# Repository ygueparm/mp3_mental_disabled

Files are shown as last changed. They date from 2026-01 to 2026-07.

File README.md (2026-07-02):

# mp3 player for mental disabled
mp3_mental_disabled is a simplified MP3 speaker designed for people with intellectual disabilities. It focuses on ease of use, minimal controls, and clear audio playback. The project aims to provide an accessible, reliable, and stress-free music experience using simple hardware and software.

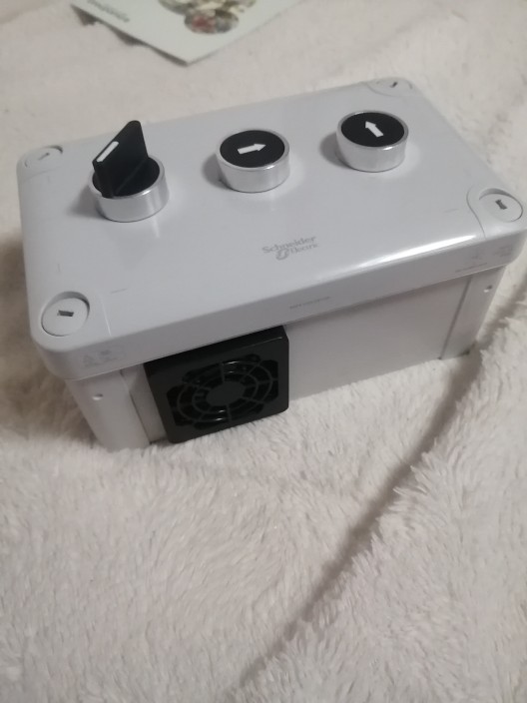
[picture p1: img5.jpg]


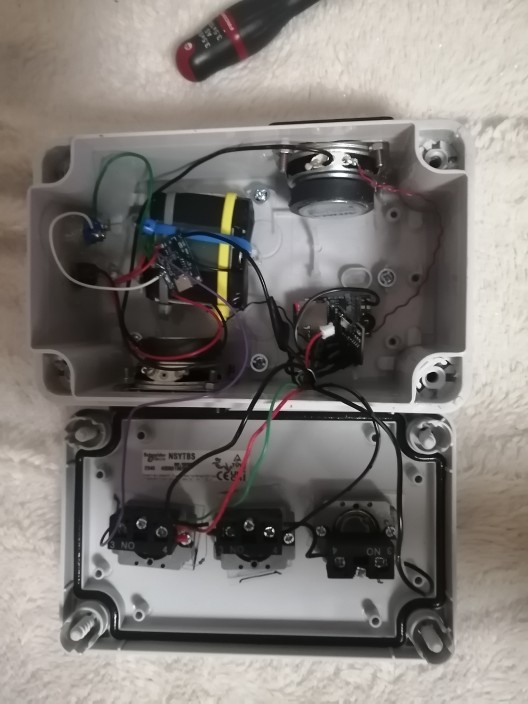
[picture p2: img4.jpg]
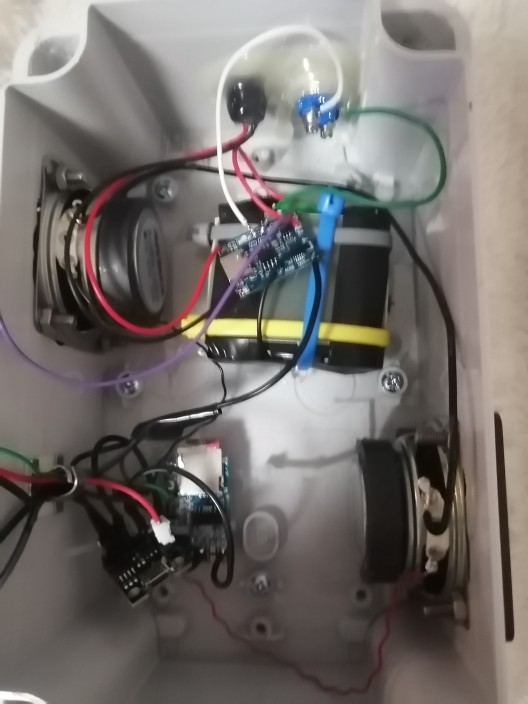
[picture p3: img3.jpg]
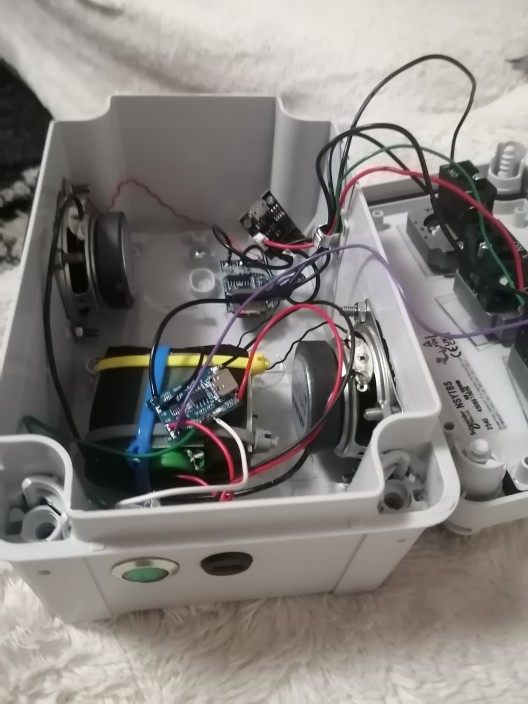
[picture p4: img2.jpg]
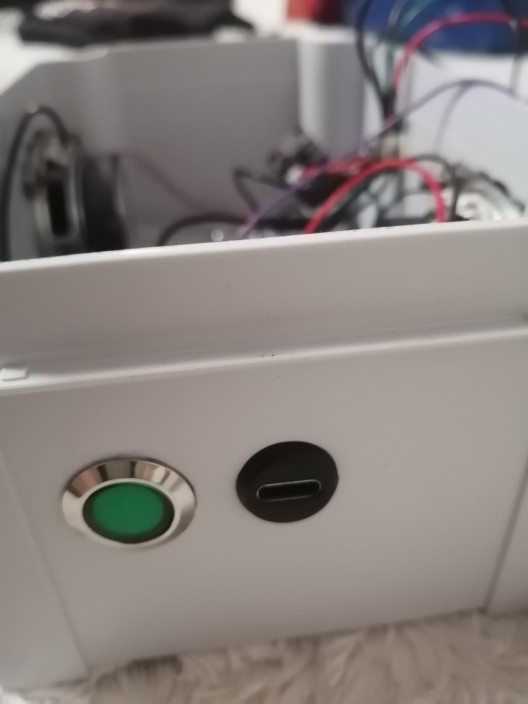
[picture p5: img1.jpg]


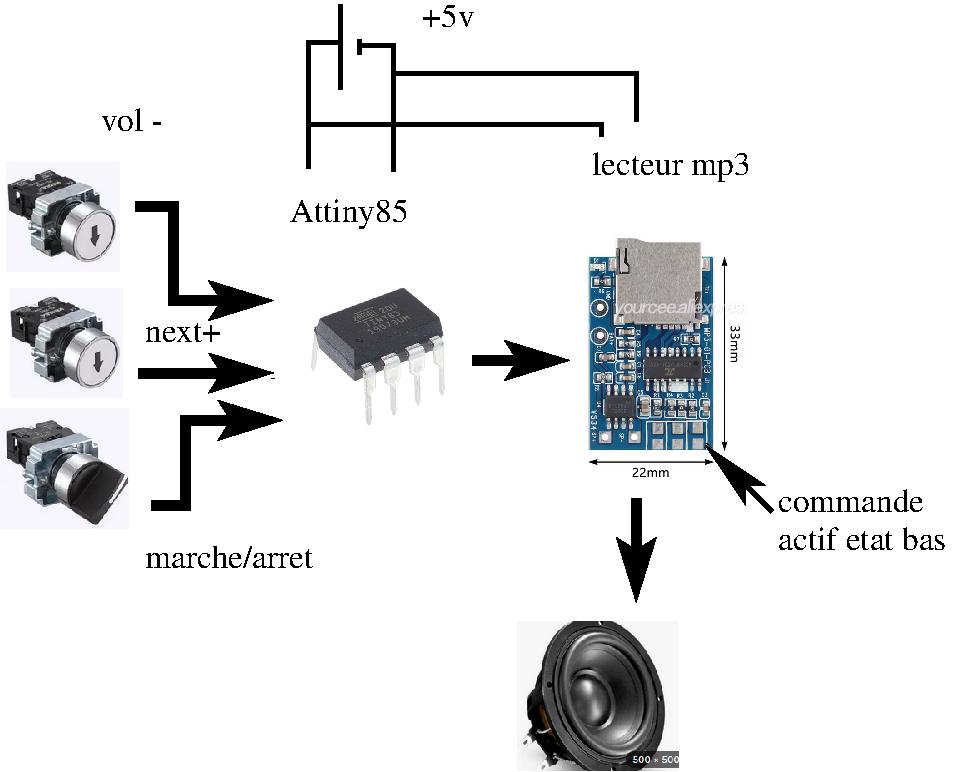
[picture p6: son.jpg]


##  MP3 Player for People with Mental Disabilities

One of my daughters is 80% mentally disabled. To give you an idea, at 20 years old she has the IQ of a 3-4 year old child.

She can learn certain things, but it takes quite a bit of time. We leave her an MP3 speaker because she loves listening to music.

The problem: These speakers have 3 buttons, and depending on how long you press them, the function changes. When she wants to change the song, she presses pretty much everything and switches the speaker to radio or Bluetooth mode, and I have to put it back in the right mode quite regularly. I don't have time for just that!

I'm using an Attiny85 as an interface between the MP3 PCB and the human to simulate the correct button presses and limit them to next+ and volume down.

I was inspired by jbd's journal at https://linuxfr.org/users/jbd/journaux/hacking-d-une-machine-a-pain
The point that was giving me trouble was using optocouplers. I found something better! No optocouplers needed!

Since the inputs are active low, I use the Tiny's LOW output, and for "no press" I set the pin as an input (so in high impedance state).

To pull to ground:
```
cpp

void setPinLow(uint8_t pin) {
  digitalWrite(pin, LOW);
  pinMode(pin, OUTPUT);
}

**Important:** set to LOW BEFORE switching to output mode

And to float (high impedance):
cpp

void setPinHighZ(uint8_t pin) {
  pinMode(pin, INPUT);
  digitalWrite(pin, LOW); // (just in case)
}
```

So no optocoupler and I'm using 4 pins out of 6 on the Tiny. At startup, I increase the volume, then I limit button presses.
The next track can only be selected after 5 seconds, so she actually listens a bit before changing :)

It's possible to completely mute the sound, but a simple power cycle restores the volume level.
To increase the volume more and more, just do several power cycles in a row.

In short: simple, effective, and it gives the person autonomy. If I tell her to stop the music, she can do it, change tracks, lower the volume too.

And she can stop it herself to go to sleep. IN SHORT: it's brilliant!

## list of equipment

### I particularly recommend the French manufacturer of polycarbonate boxes, which are resistant and unbreakable schneider electrique :
The cover is closed with four captive flat screws located outside the sealed area of the enclosure to maintain the IP rating. It is TÜV and UL certified and is fire resistant up to 960°C in accordance with IEC 62208. It offers high protection against dust and water with an IP66 rating (NEMA 4.4X). It is impact resistant (IK08 rating, IEC 62262). It also has Class II electrical insulation, which prevents electric shocks and offers fully insulated solutions. It can be stored at temperatures between -15 and 60°C and used between -25 and 80°C without affecting its performance. you can use it even in siberia ! :)

 *  https://www.se.com/fr/fr/product/NSYTBP16128/panelset-bo%C3%AEte-industrielle-164x121x87mm-pc/
 *  PanelSeT - boîte industrielle - 164x121x87mm - PCNSYTBP16128

 *  1Pcs Metal Round Socket Module
 *  https://fr.aliexpress.com/item/1005005363341111.html

 *  AIYIMA 2 pièces 2 "pouces 4 Ohm 3W gamme
 *  https://fr.aliexpress.com/item/32593991938.html

 *  https://fr.aliexpress.com/item/1005007445592831.html
 * 
 *  Ttiny85 Digispark Kickstarter Micro USB
 *  https://fr.aliexpress.com/item/1005009004637470.html

 *  Audio MP3 TF 2W 5V
 *  https://fr.aliexpress.com/item/1005009187267335.html

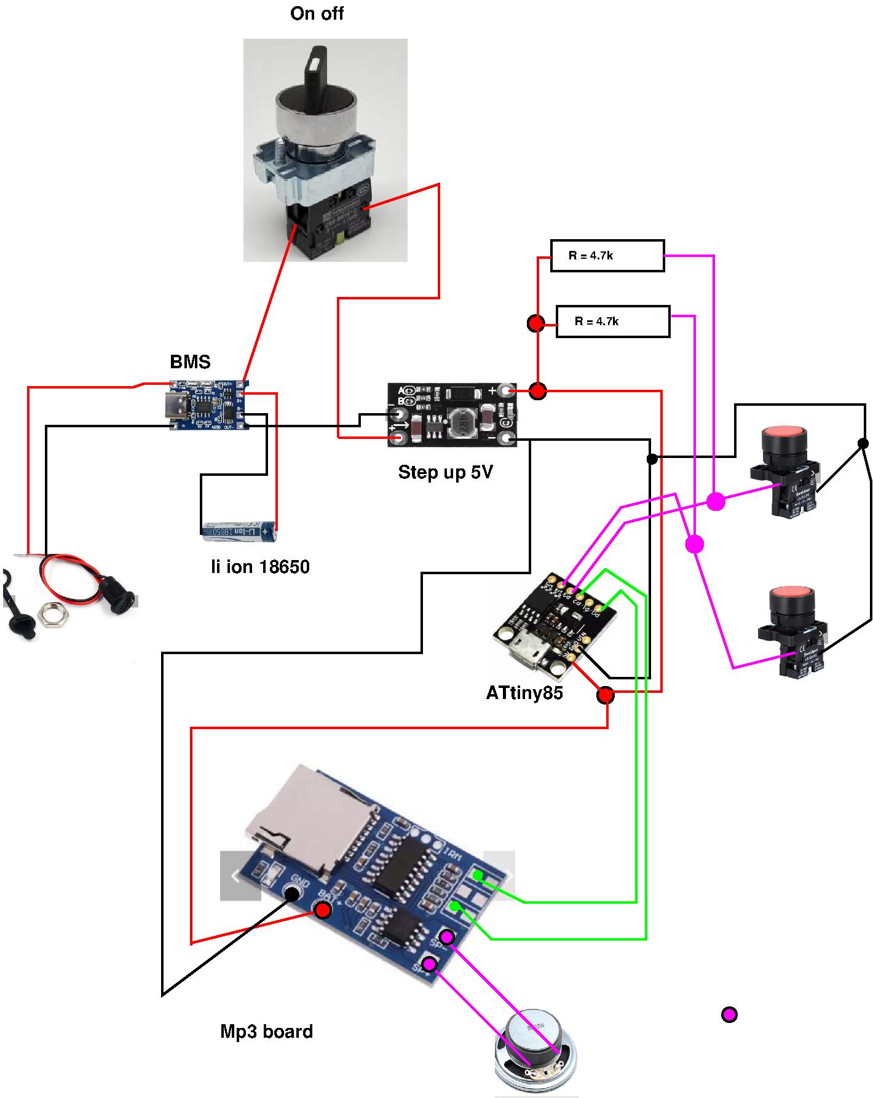
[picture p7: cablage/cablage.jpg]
blue print


Why choose the Tiny85? I always feel a bit bad using only 4 pins out of 40 on a microcontroller. Low power consumption, 1MHz speed, variable supply voltage. Very flexible to use and very cheap. A bit difficult to program because you need an Arduino in ISP mode as an interface between the Tiny and Arduino IDE.

# Small production
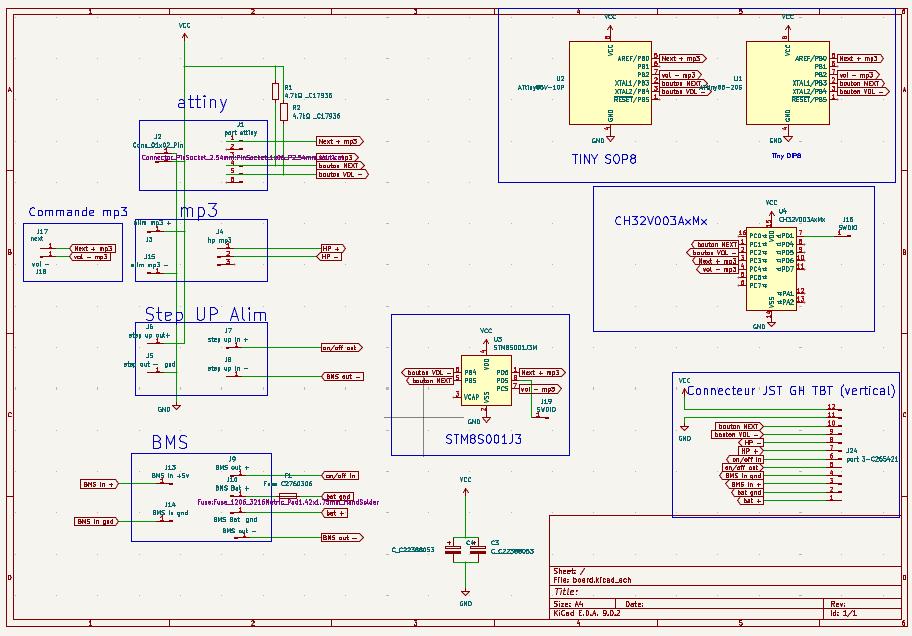
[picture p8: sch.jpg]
sch

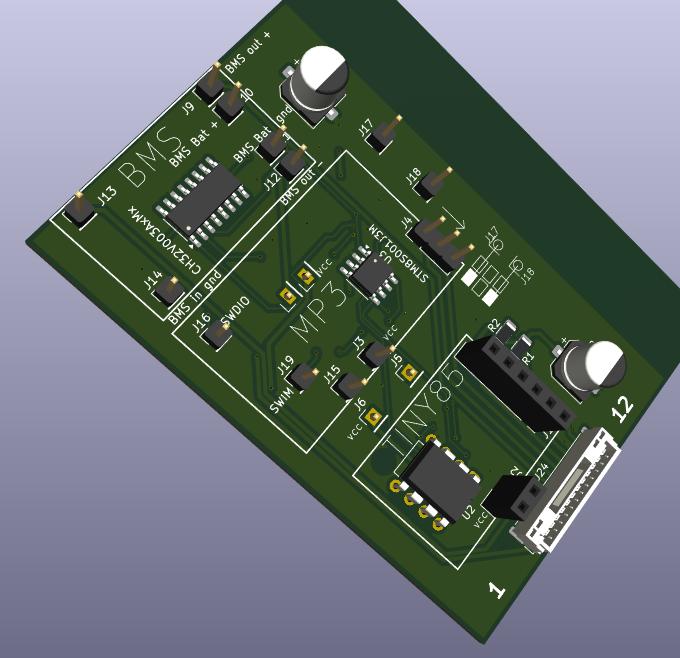
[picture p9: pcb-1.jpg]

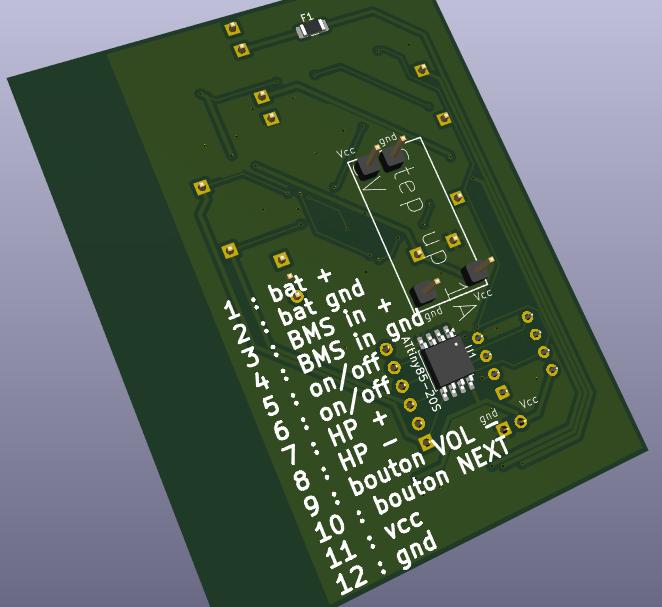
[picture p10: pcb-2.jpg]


Now the project is very well and my daughter is very happy but it take 2 to 3 hours to make one, for small production i made a mother board
for reduce the time for it. time to time and buold one for this friends, and some young children like it very much (2 to 5 years old) !

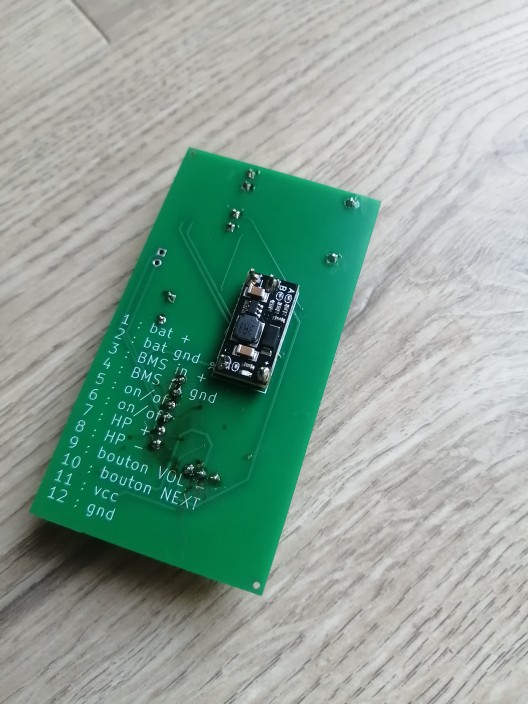
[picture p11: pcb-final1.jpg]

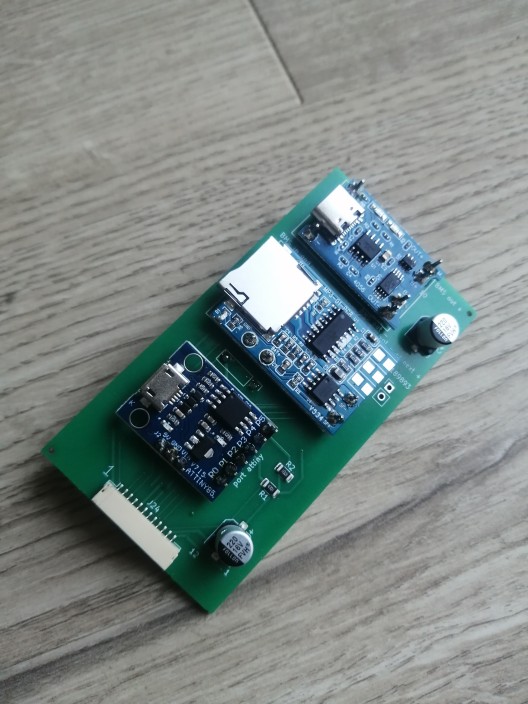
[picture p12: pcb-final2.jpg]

 
 this pcb can spped up your box, only 10 to 15 min to finish one instead 2 a 3h, this pcb let you choose wich chip you prefer, small board with Attiny85, chip attiny85, STM8, CH32V003A4M6, the last one cost only 0.20€ and you can use arduino-ide for programming it
 
 YOU NEED ONLY ONE OF THIS CHIP AT ONCE : attiny85, STM8, CH32V003A4M6 simply choose wich you prefer

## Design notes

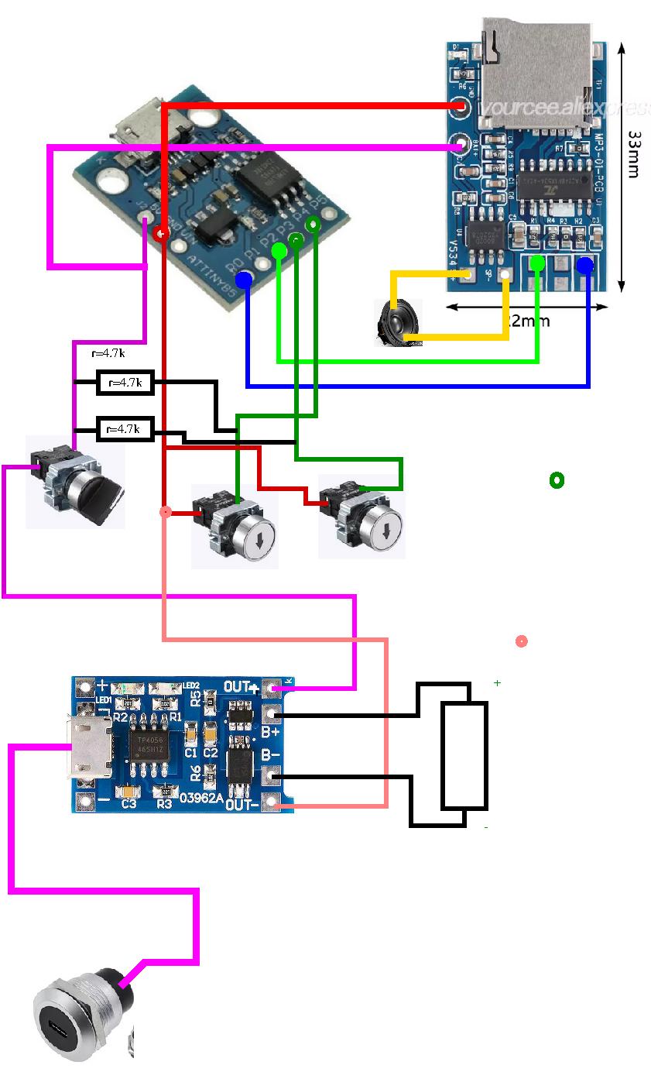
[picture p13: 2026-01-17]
plan.jpg

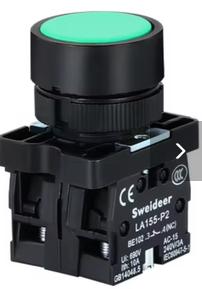
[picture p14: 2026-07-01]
cablage/bouton.jpg

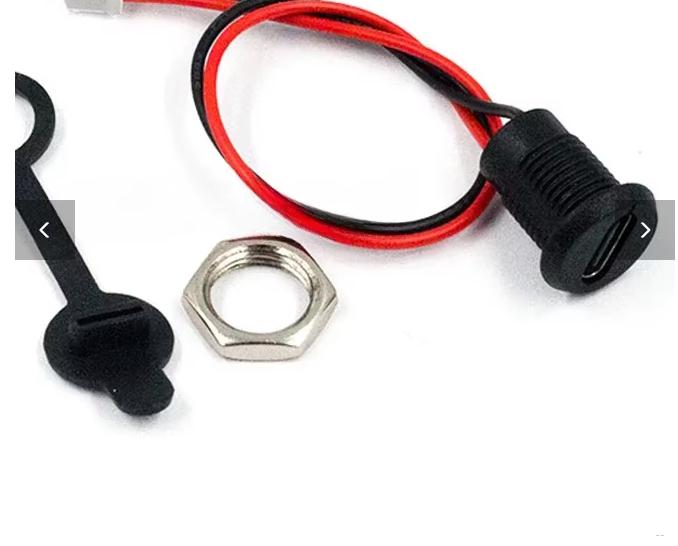
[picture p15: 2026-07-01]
cablage/usbc-prise.jpg

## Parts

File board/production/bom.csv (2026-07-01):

Designator | Footprint | Quantity | Value | LCSC Part #
C3, C4 | CP_Elec_6.3x7.7 | 2 | C_C22388053
F1 | 1206 | 1 | Fuse C2760306
J1 | PinSocket_1x06_P2.54mm_Vertical | 1 | port attiny
J10 | PinHeader_1x01_P2.54mm_Vertical | 1 | BMS Bat +
J11 | PinHeader_1x01_P2.54mm_Vertical | 1 | BMS Bat gnd
J12 | PinHeader_1x01_P2.54mm_Vertical | 1 | BMS out -
J13 | PinHeader_1x01_P2.54mm_Vertical | 1 | BMS in +5v
J14 | PinHeader_1x01_P2.54mm_Vertical | 1 | BMS in gnd
J15 | PinHeader_1x01_P2.54mm_Vertical | 1 | alim mp3 -
J16 | PinHeader_1x01_P2.54mm_Vertical | 1 | SWDIO
J17 | PinHeader_1x01_P2.54mm_Vertical | 1 | next
J18 | PinHeader_1x01_P2.54mm_Vertical | 1 | vol -
J19 | PinHeader_1x01_P2.54mm_Vertical | 1 | SWIM
J2 | PinSocket_1x02_P2.54mm_Vertical | 1 | Conn_01x02_Pin
J24 | JST_GH_BM12B-GHS-TBT_1x12-1MP_P1.25mm_Vertical | 1 | port 3-C265421
J3 | PinHeader_1x01_P2.54mm_Vertical | 1 | alim mp3 +
J4 | PinHeader_1x03_P2.54mm_Vertical-mp3 | 1 | hp mp3
J5 | PinHeader_1x01_P2.54mm_Vertical | 1 | step out - gnd
J6 | PinHeader_1x01_P2.54mm_Vertical | 1 | step up out+
J7 | PinHeader_1x01_P2.54mm_Vertical | 1 | step up in +
J8 | PinHeader_1x01_P2.54mm_Vertical | 1 | step up in -
J9 | PinHeader_1x01_P2.54mm_Vertical | 1 | BMS out +
R1, R2 | 1206 | 2 | 4.7kΩ _C17936
U1 | SOIC-8_5.3x5.3mm_P1.27mm | 1 | ATtiny85-20S
U2 | DIP-8_W7.62mm | 1 | ATtiny85V-10P
U3 | SO-8_3.9x4.9mm_P1.27mm | 1 | STM8S001J3M
U4 | SOP-16_3.9x9.9mm_P1.27mm | 1 | CH32V003AxMx

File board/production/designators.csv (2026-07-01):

C3:1
C4:1
F1:1
J1:1
J10:1
J11:1
J12:1
J13:1
J14:1
J15:1
J16:1
J17:1
J18:1
J19:1
J2:1
J24:1
J3:1
J4:1
J5:1
J6:1
J7:1
J8:1
J9:1
R1:1
R2:1
U1:1
U2:1
U3:1
U4:1

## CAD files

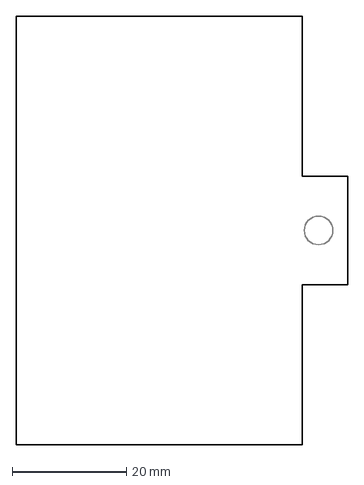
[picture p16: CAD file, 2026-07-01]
board/pcb.dxf
58.0 x 75.0 mm

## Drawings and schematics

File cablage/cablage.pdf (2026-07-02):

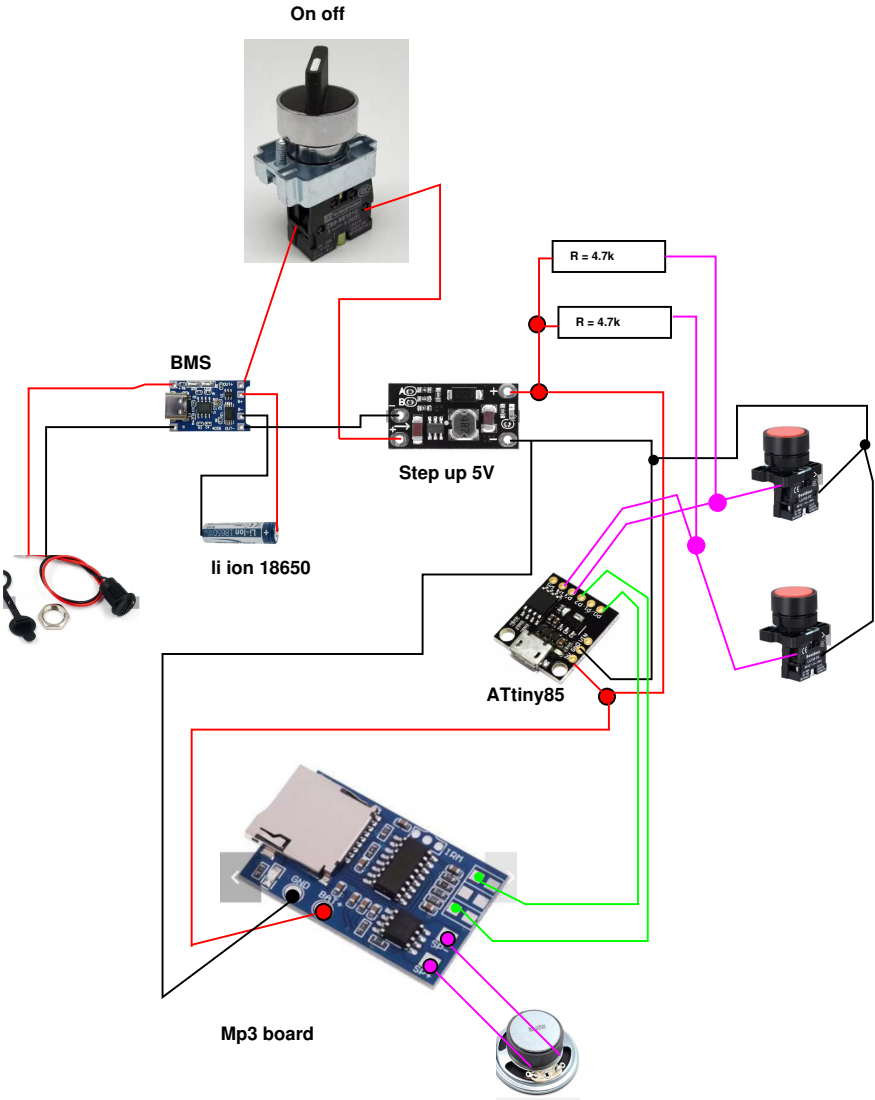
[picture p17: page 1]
Step up 5V; li ion 18650; Mp3 board; ATtiny85; BMS; On off

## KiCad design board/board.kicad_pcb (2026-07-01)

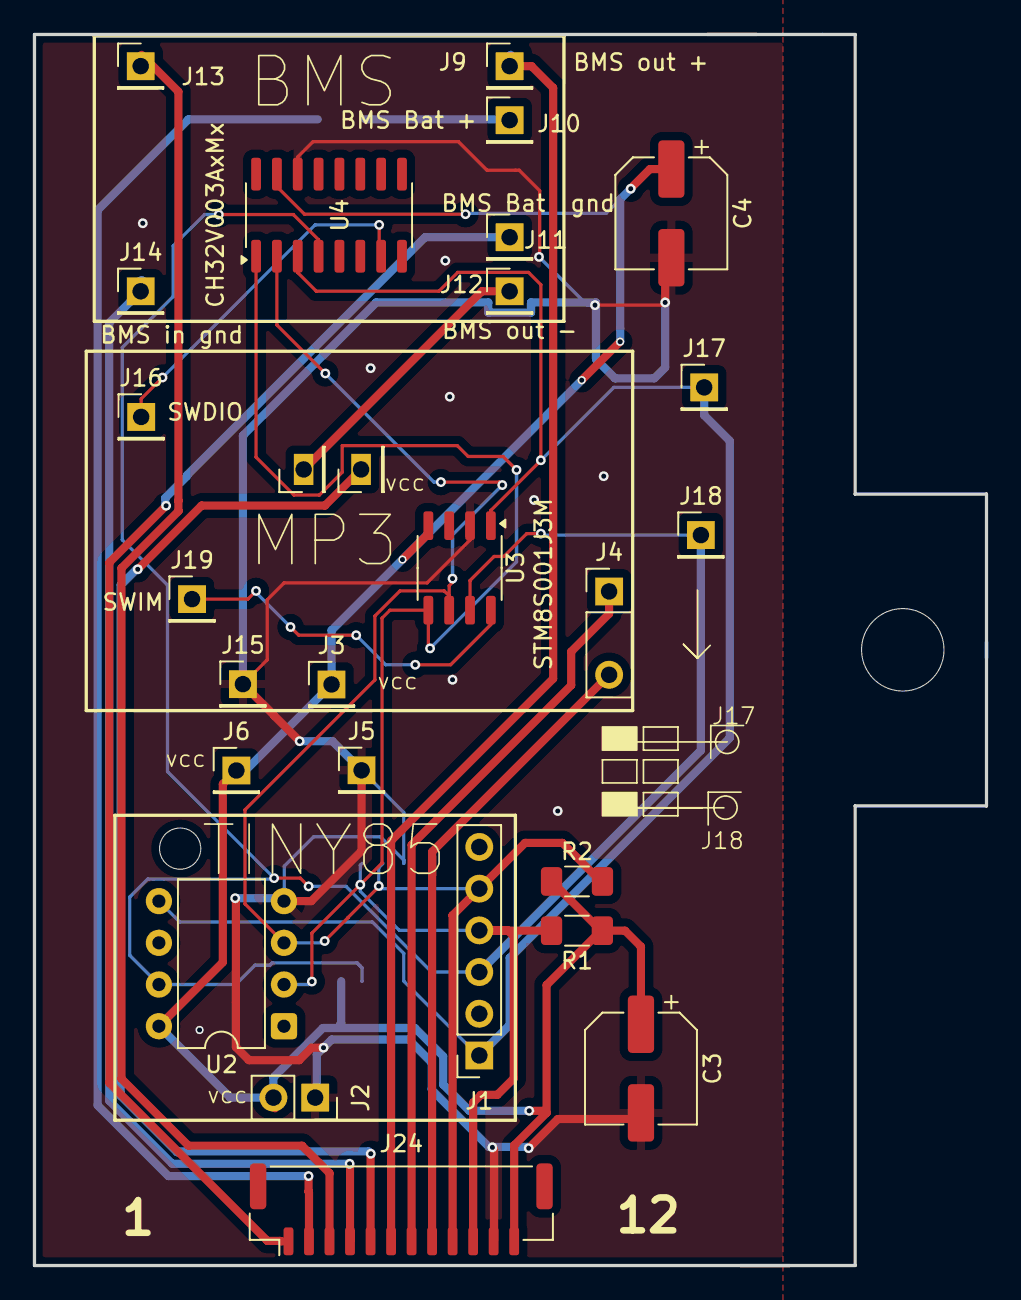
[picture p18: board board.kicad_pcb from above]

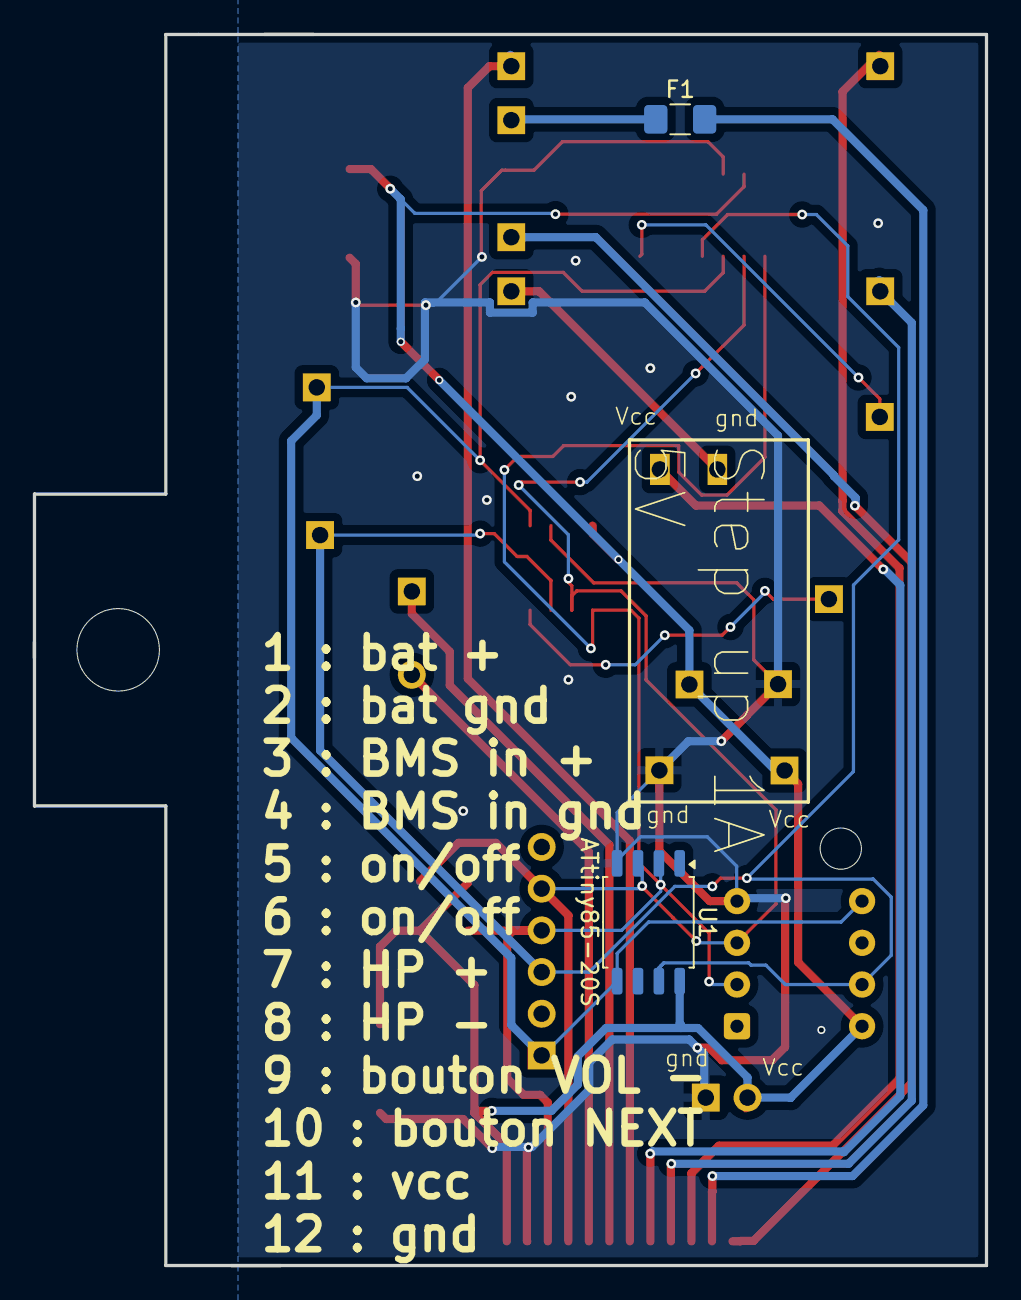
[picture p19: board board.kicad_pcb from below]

Board: 2 copper layers, 58.0 x 75.0 mm, 29 parts (2 on the bottom side), 18 nets.

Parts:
C3, C4: C_C22388053; CP_Elec_6.3x7.7
F1: Fuse C2760306; Fuse_1206_3216Metric_Pad1.42x1.75mm_HandSolder
J1: port attiny; PinSocket_1x06_P2.54mm_Vertical
J2: Conn_01x02_Pin; PinSocket_1x02_P2.54mm_Vertical
J3: alim mp3 +; PinHeader_1x01_P2.54mm_Vertical
J4: hp mp3; PinHeader_1x03_P2.54mm_Vertical-mp3
J5: step out - gnd; PinHeader_1x01_P2.54mm_Vertical
J6: step up out+; PinHeader_1x01_P2.54mm_Vertical
J7: step up in +; PinHeader_1x01_P2.54mm_Vertical
J8: step up in -; PinHeader_1x01_P2.54mm_Vertical
J9: BMS out +; PinHeader_1x01_P2.54mm_Vertical
J10: BMS Bat +; PinHeader_1x01_P2.54mm_Vertical
J11: BMS Bat gnd; PinHeader_1x01_P2.54mm_Vertical
J12: BMS out -; PinHeader_1x01_P2.54mm_Vertical
J13: BMS in +5v; PinHeader_1x01_P2.54mm_Vertical
J14: BMS in gnd; PinHeader_1x01_P2.54mm_Vertical
J15: alim mp3 -; PinHeader_1x01_P2.54mm_Vertical
J16: SWDIO; PinHeader_1x01_P2.54mm_Vertical
J17: next; PinHeader_1x01_P2.54mm_Vertical
J18: vol -; PinHeader_1x01_P2.54mm_Vertical
J19: SWIM; PinHeader_1x01_P2.54mm_Vertical
J24: port 3-C265421; JST_GH_BM12B-GHS-TBT_1x12-1MP_P1.25mm_Vertical
R1, R2: 4.7kΩ _C17936; R_1206_3216Metric_Pad1.30x1.75mm_HandSolder
U1: ATtiny85-20S; SOIC-8_5.3x5.3mm_P1.27mm
U2: ATtiny85V-10P; DIP-8_W7.62mm
U3: STM8S001J3M; SO-8_3.9x4.9mm_P1.27mm
U4: CH32V003AxMx; SOP-16_3.9x9.9mm_P1.27mm

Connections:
BMS in +: J13.1, J24.3
BMS in gnd: J14.1, J24.4
BMS out -: J8.1, J12.1
GND: C3.2, C4.2, J2.1, J5.1, J15.1, J24.11, U1.4 (GND), U2.4 (GND), U3.2 (VSS), U4.14 (VSS)
HP +: J4.1, J24.7
HP -: J4.2, J24.8
unnamed: F1.1, J10.1
unnamed: J16.1, U4.7 (PD1)
unnamed: J19.1, U3.8 (PD5)
Next + mp3: J1.1, J17.1, U1.5 (AREF/PB0), U2.5 (AREF/PB0), U3.1 (PD6), U4.3 (PC3)
VCC: C3.1, C4.1, J2.2, J3.1, J6.1, J24.12, R1.1, R2.1, U1.8 (VCC), U2.8 (VCC), U3.4 (VDD), U4.15 (VDD)
bat +: J11.1, J24.1
bat gnd: F1.2, J24.2
bouton NEXT: J1.4, J24.10, R1.2, U1.2 (XTAL1/PB3), U2.2 (XTAL1/PB3), U3.5 (PB5), U4.1 (PC1)
bouton VOL -: J1.5, J24.9, R2.2, U1.3 (XTAL2/PB4), U2.3 (XTAL2/PB4), U3.6 (PB4), U4.2 (PC2)
on/off in: J9.1, J24.6
on/off out: J7.1, J24.5
vol - mp3: J1.3, J18.1, U1.7 (PB2), U2.7 (PB2), U3.7 (PC5), U4.4 (PC4)

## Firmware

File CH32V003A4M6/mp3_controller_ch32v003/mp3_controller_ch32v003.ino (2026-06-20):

/*
 * Contrôleur MP3 Minimaliste — CH32V003A4M6
 * Transposé depuis ATtiny85 v3.4
 * Architecture: RISC-V 32 bits, 48 MHz (réduit à ~1 MHz via prescaler)
 *
 * === MAPPING DES BROCHES ===
 *
 * | Fonction        | ATtiny85 | CH32V003A4M6 | Broche physique |
 * |-----------------|----------|--------------|-----------------|
 * | Bouton Next     | PB3      | C1 (PC1)     | pin 1           |
 * | Bouton Vol-     | PB4      | C2 (PC2)     | pin 2           |
 * | Sortie KEY      | PB2      | C3 (PC3)     | pin 3           |
 * | Sortie KEY_VOL- | PB0      | C4 (PC4)     | pin 4           |
 *
 * === NOTES D'ADAPTATION ===
 * - Le CH32V003 n'a pas de mode 1 MHz natif. On garde 48 MHz mais
 *   les délais restent corrects grâce à delay() qui est calibré.
 * - Open-drain : le CH32V003 supporte le mode OUTPUT_OPEN_DRAIN
 *   via pinMode(pin, OUTPUT_OPEN_DRAIN). Si ton core ne le supporte
 *   pas, la méthode setPinLow/setPinHighZ reste compatible.
 * - Les numéros de broches ci-dessous suivent la numérotation
 *   Arduino du core CH32 WCH. Adapte si tu utilises ch32v003fun.
 *
 * === ALIMENTATION ===
 * - 3.3V (idem ATtiny85 en 3.3V)
 * - Consommation plus élevée qu'ATtiny85 (~5 mA actif vs ~0.3 mA)
 */

// --- Broches (numérotation Arduino, core CH32 WCH) ---
// PD4 = Arduino pin 4 sur CH32V003 (à vérifier selon ton core)
const uint8_t BTN_NEXT    = C1;   // Bouton Next Track (entrée, pull-up)
const uint8_t BTN_VOL_D   = C2;   // Bouton Volume -   (entrée, pull-up)
const uint8_t KEY_TRACK   = C3;   // Sortie vers KEY du MP3 (Next / Vol+)
const uint8_t KEY_VOLDOWN = C4;   // Sortie vers KEY_VOLDOWN du MP3

// --- Durées de pulse (inchangées) ---
const uint16_t PULSE_NEXT     = 250;   // ms — next track sur KEY_TRACK
const uint16_t PULSE_VOL_UP   = 2500;  // ms — volume + sur KEY_TRACK (setup)
const uint16_t PULSE_VOL_DOWN = 1500;  // ms — volume - sur KEY_VOLDOWN

// --- Timing ---
const uint16_t MP3_BOOT_DELAY  = 1000; // ms — attente démarrage module MP3
const uint16_t DEBOUNCE_DELAY  = 50;   // ms — anti-rebond
const uint16_t COOLDOWN_NEXT   = 4000; // ms — délai min entre deux Next
const uint16_t COOLDOWN_VOL_D  = 2000; // ms — délai min entre deux Vol-

// --- État bouton Next ---
uint8_t  lastBtnStateNext    = HIGH;
uint32_t lastDebounceTimeNext = 0;
uint8_t  btnStateNext         = HIGH;
uint32_t lastActionTimeNext   = 0;

// --- État bouton Vol- ---
uint8_t  lastBtnStateVolD    = HIGH;
uint32_t lastDebounceTimeVolD = 0;
uint8_t  btnStateVolD         = HIGH;
uint32_t lastActionTimeVolD   = 0;

// ---------------------------------------------------------------------------
// Pilotage open-drain : LOW actif, haute impédance au repos
// Compatible avec les deux méthodes (OUTPUT_OPEN_DRAIN ou INPUT flottant)
// ---------------------------------------------------------------------------

void setPinLow(uint8_t pin) {
    digitalWrite(pin, LOW);
    pinMode(pin, OUTPUT);
}

void setPinHighZ(uint8_t pin) {
    pinMode(pin, INPUT);      // haute impédance — la résistance de tirage
    digitalWrite(pin, LOW);   // du module MP3 remonte la ligne
}

void setPinInput(uint8_t pin) {
    pinMode(pin, INPUT_PULLUP);
}

// Génère une impulsion LOW de durée 'duration' ms
void sendPulse(uint8_t pin, uint16_t duration) {
    setPinLow(pin);
    delay(duration);
    setPinHighZ(pin);
}

// ---------------------------------------------------------------------------
// Anti-rebond + détection front descendant (HIGH → LOW)
// Identique à l'ATtiny85 — millis() fonctionne de la même façon
// ---------------------------------------------------------------------------

bool buttonFell(uint8_t pin,
                uint8_t  &lastState,
                uint32_t &lastDebounceTime,
                uint8_t  &currentState)
{
    uint8_t  reading = digitalRead(pin);
    uint32_t now     = millis();

    if (reading != lastState) {
        lastDebounceTime = now;
    }

    if ((now - lastDebounceTime) > DEBOUNCE_DELAY) {
        if (reading != currentState) {
            currentState = reading;
            if (currentState == LOW) {
                lastState = reading;
                return true;
            }
        }
    }

    lastState = reading;
    return false;
}

// Vérifie que le cooldown est écoulé depuis la dernière action
bool canTriggerAction(uint32_t &lastActionTime, uint16_t cooldownDelay) {
    uint32_t now = millis();

    // Gestion débordement millis() (~49 jours)
    if (now < lastActionTime) {
        lastActionTime = now;
        return true;
    }

    return ((now - lastActionTime) >= cooldownDelay);
}

// ---------------------------------------------------------------------------
// Setup
// ---------------------------------------------------------------------------

void setup() {
    // Entrées avec pull-up interne
    setPinInput(BTN_NEXT);
    setPinInput(BTN_VOL_D);

    // Sorties en haute impédance au repos
    setPinHighZ(KEY_VOLDOWN);
    setPinHighZ(KEY_TRACK);

    // Lecture initiale des boutons
    lastBtnStateNext = digitalRead(BTN_NEXT);
    lastBtnStateVolD = digitalRead(BTN_VOL_D);
    btnStateNext     = lastBtnStateNext;
    btnStateVolD     = lastBtnStateVolD;

    // Init des timers
    uint32_t now       = millis();
    lastDebounceTimeNext = now;
    lastDebounceTimeVolD = now;
    lastActionTimeNext   = 0;
    lastActionTimeVolD   = 0;

    // Attendre le démarrage du module MP3
    delay(MP3_BOOT_DELAY);

    // Augmentation volume au démarrage (décommenter si nécessaire)
    // sendPulse(KEY_TRACK, PULSE_VOL_UP);
    // delay(500);
}

// ---------------------------------------------------------------------------
// Boucle principale (identique à l'ATtiny85)
// ---------------------------------------------------------------------------

void loop() {
    // Bouton Next Track (cooldown 4 s)
    if (buttonFell(BTN_NEXT, lastBtnStateNext, lastDebounceTimeNext, btnStateNext)) {
        if (canTriggerAction(lastActionTimeNext, COOLDOWN_NEXT)) {
            sendPulse(KEY_TRACK, PULSE_NEXT);
            lastActionTimeNext = millis();
        }
    }

    // Bouton Volume - (cooldown 2 s)
    if (buttonFell(BTN_VOL_D, lastBtnStateVolD, lastDebounceTimeVolD, btnStateVolD)) {
        if (canTriggerAction(lastActionTimeVolD, COOLDOWN_VOL_D)) {
            sendPulse(KEY_VOLDOWN, PULSE_VOL_DOWN);
            lastActionTimeVolD = millis();
        }
    }

    delay(5);
}

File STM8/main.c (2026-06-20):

/*
 * Contrôleur MP3 Minimaliste — STM8S001J3
 * Porté depuis ATtiny85 v3.4
 *
 * Toolchain : SDCC + stm8flash
 * Compilé avec : sdcc -mstm8 --std-sdcc11 main.c
 * Flashé avec  : stm8flash -c stlinkv2 -p stm8s001j3 -w main.ihx
 *
 * Mapping des broches (boîtier SO8) :
 *  PD5 (pin 1) → BTN_NEXT    (entrée, pull-up interne)
 *  PA1 (pin 2) → non utilisé  (sortie push-pull, forcée à 0)
 *  PA2 (pin 3) → non utilisé  (sortie push-pull, forcée à 0)
 *  PA3 (pin 4) → non utilisé  (sortie push-pull, forcée à 0)
 *  PC3 (pin 5) → KEY_VOLDOWN (sortie open-drain)
 *  PC4 (pin 6) → KEY_TRACK   (sortie open-drain)
 *  PC5 (pin 7) → BTN_VOL_D   (entrée, pull-up interne) ← SWIM libre sur PD1
 *  PD6 (pin 8) → non utilisé  (sortie push-pull, forcée à 0)
 *
 * Horloge : HSI 16 MHz / 32 = 500 kHz (CLK_CKDIVR = 0x1B)
 *
 * Timer : TIM4 génère une interruption toutes les 1 ms
 *         → tick_ms est incrémenté UNIQUEMENT dans l'ISR, jamais dans delay_ms.
 *         → millis() et les cooldowns sont donc exacts même pendant send_pulse.
 */

#include <stdint.h>

/* ------------------------------------------------------------------ */
/* Registres STM8S001J3                                                */
/* ------------------------------------------------------------------ */

/* Horloge */
#define CLK_CKDIVR   (*(volatile uint8_t*)0x50C6)

/* Port A */
#define PA_ODR       (*(volatile uint8_t*)0x5000)
#define PA_DDR       (*(volatile uint8_t*)0x5002)
#define PA_CR1       (*(volatile uint8_t*)0x5003)
#define PA_CR2       (*(volatile uint8_t*)0x5004)

/* Port C */
#define PC_IDR       (*(volatile uint8_t*)0x500B)
#define PC_ODR       (*(volatile uint8_t*)0x500A)
#define PC_DDR       (*(volatile uint8_t*)0x500C)
#define PC_CR1       (*(volatile uint8_t*)0x500D)
#define PC_CR2       (*(volatile uint8_t*)0x500E)

/* Port D */
#define PD_IDR       (*(volatile uint8_t*)0x5011)
#define PD_ODR       (*(volatile uint8_t*)0x5010)
#define PD_DDR       (*(volatile uint8_t*)0x5013)
#define PD_CR1       (*(volatile uint8_t*)0x5014)
#define PD_CR2       (*(volatile uint8_t*)0x5015)

/*
 * TIM4 — timer 8 bits, parfait pour timebase 1 ms
 *   TIM4_CR1  : contrôle (bit 0 = CEN, active le compteur)
 *   TIM4_IER  : interrupt enable (bit 0 = UIE, débordement)
 *   TIM4_SR   : status (bit 0 = UIF, flag débordement)
 *   TIM4_PSCR : prescaler (valeur = 2^N)
 *   TIM4_ARR  : auto-reload (valeur max du compteur)
 */
#define TIM4_CR1     (*(volatile uint8_t*)0x5340)
#define TIM4_IER     (*(volatile uint8_t*)0x5343)
#define TIM4_SR      (*(volatile uint8_t*)0x5344)
#define TIM4_PSCR    (*(volatile uint8_t*)0x5347)
#define TIM4_ARR     (*(volatile uint8_t*)0x5348)

/* Interruptions */
#define enableInterrupts()  __asm__("rim")
#define disableInterrupts() __asm__("sim")

/* ------------------------------------------------------------------ */
/* Broches                                                             */
/* ------------------------------------------------------------------ */

#define BTN_NEXT_BIT     5   /* PD5 — bouton Next Track  */
#define BTN_VOLD_BIT     5   /* PC5 — bouton Volume -    */
#define KEY_VOLDOWN_BIT  3   /* PC3 — sortie vol-        */
#define KEY_TRACK_BIT    4   /* PC4 — sortie next/vol+   */

#define BTN_NEXT_READ()   ((PD_IDR >> BTN_NEXT_BIT) & 1)
#define BTN_VOLD_READ()   ((PC_IDR >> BTN_VOLD_BIT) & 1)

/* ------------------------------------------------------------------ */
/* Timebase — TIM4 ISR                                                 */
/* ------------------------------------------------------------------ */

static volatile uint32_t tick_ms = 0;

/*
 * ISR TIM4 — vecteur 23 sur STM8S
 */
void TIM4_UPD_OVF_IRQHandler(void) __interrupt(23)
{
    TIM4_SR &= ~0x01;   /* acquitter le flag UIF */
    tick_ms++;
}

/*
 * Lecture atomique de tick_ms (IRQ coupées le temps de lire les 4 octets,
 * indispensable sur architecture 8 bits).
 */
static uint32_t millis(void)
{
    uint32_t val;
    disableInterrupts();
    val = tick_ms;
    enableInterrupts();
    return val;
}

/* ------------------------------------------------------------------ */
/* Délai bloquant — tick_ms avance via l'ISR, pas ici                 */
/* ------------------------------------------------------------------ */

static void delay_ms(uint16_t ms)
{
    uint32_t start = millis();
    while ((millis() - start) < ms) {
        /* attente active */
    }
}

/* ------------------------------------------------------------------ */
/* Durées                                                              */
/* ------------------------------------------------------------------ */

#define PULSE_NEXT       250U
#define PULSE_VOL_UP    2500U
#define PULSE_VOL_DOWN  1500U
#define MP3_BOOT_DELAY  1000U
#define DEBOUNCE_DELAY    50U
#define COOLDOWN_NEXT   4000U
#define COOLDOWN_VOLD   2000U

/* ------------------------------------------------------------------ */
/* État des boutons                                                    */
/* ------------------------------------------------------------------ */

static uint8_t  lastStateNext  = 1;
static uint8_t  btnStateNext   = 1;
static uint32_t debounceNext   = 0;
static uint32_t lastActionNext = 0;

static uint8_t  lastStateVolD  = 1;
static uint8_t  btnStateVolD   = 1;
static uint32_t debounceVolD   = 0;
static uint32_t lastActionVolD = 0;

/* ------------------------------------------------------------------ */
/* Helpers open-drain                                                  */
/* ------------------------------------------------------------------ */

static void pin_low(uint8_t is_track)
{
    if (is_track) {
        PC_ODR &= ~(1 << KEY_TRACK_BIT);
        PC_DDR |=  (1 << KEY_TRACK_BIT);
    } else {
        PC_ODR &= ~(1 << KEY_VOLDOWN_BIT);
        PC_DDR |=  (1 << KEY_VOLDOWN_BIT);
    }
}

static void pin_hiz(uint8_t is_track)
{
    if (is_track) {
        PC_DDR &= ~(1 << KEY_TRACK_BIT);
        PC_CR1 &= ~(1 << KEY_TRACK_BIT);
    } else {
        PC_DDR &= ~(1 << KEY_VOLDOWN_BIT);
        PC_CR1 &= ~(1 << KEY_VOLDOWN_BIT);
    }
}

static void send_pulse(uint8_t is_track, uint16_t duration_ms)
{
    pin_low(is_track);
    delay_ms(duration_ms);
    pin_hiz(is_track);
}

/* ------------------------------------------------------------------ */
/* Détection front descendant avec anti-rebond                        */
/* ------------------------------------------------------------------ */

static uint8_t button_fell(uint8_t reading,
                            uint8_t  *lastState,
                            uint32_t *debounceTime,
                            uint8_t  *currentState)
{
    uint32_t now = millis();

    if (reading != *lastState)
        *debounceTime = now;

    /* Soustraction non signée : correct même en cas de débordement 32 bits */
    if ((now - *debounceTime) > DEBOUNCE_DELAY) {
        if (reading != *currentState) {
            *currentState = reading;
            if (*currentState == 0) {
                *lastState = reading;
                return 1;
            }
        }
    }

    *lastState = reading;
    return 0;
}

/* ------------------------------------------------------------------ */
/* Vérification cooldown                                               */
/* ------------------------------------------------------------------ */

static uint8_t can_trigger(uint32_t *lastActionTime, uint16_t cooldown)
{
    /* Soustraction non signée : robuste au débordement */
    if ((millis() - *lastActionTime) >= cooldown)
        return 1;
    return 0;
}

/* ------------------------------------------------------------------ */
/* Initialisation TIM4 pour 1 ms à 500 kHz                            */
/*                                                                     */
/* F_CPU = 500 000 Hz                                                  */
/* Prescaler /8  → F_tim = 62 500 Hz → période = 16 µs               */
/* ARR = 62 → débordement toutes les 63 × 16 µs = 1,008 ms ≈ 1 ms    */
/* ------------------------------------------------------------------ */

static void tim4_init(void)
{
    TIM4_CR1  = 0x00;
    TIM4_PSCR = 0x03;   /* prescaler /8 (2^3)           */
    TIM4_ARR  = 62;     /* auto-reload : compte de 0→62 */
    TIM4_IER  = 0x01;   /* interruption débordement     */
    TIM4_SR   = 0x00;   /* acquitter flag résiduel      */
    TIM4_CR1  = 0x01;   /* démarrer (CEN=1)             */
}
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

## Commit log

2026-04-30 pcb carte mere
    [board.kicad_pcb, board.kicad_sch]
2026-05-01 ajout +5v + resistance de tirage
    [board.kicad_pcb, board.kicad_sch]
2026-05-03 pcb carte mere mise a jour
    [board.kicad_sch, bom.csv, designators.csv, positions.csv]
2026-05-03 copie ecran pcb + modif positionnement pad
    [board.kicad_pcb, bom.csv, designators.csv, positions.csv]
2026-05-03 copie ecran new pcb
2026-05-21 mise a jour pcb
    [board-RA.kicad_sch, board.kicad_pcb, bom.csv, designators.csv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]
2026-05-22 correction pcb , ajout copie d'ecran, et modification readme
    [board.kicad_pcb]
2026-05-22 correction sens pin vue 3D
    [board.kicad_sch]
2026-05-22 ajout serigraphie pour faciliter le montage
    [board.kicad_pcb, board.kicad_sch]
2026-05-22 mise a jour marquage pcb et ajout programation tiny dans le source
    [board.kicad_pcb]
2026-05-25 ajout connecteur programmation tiny85
    [board.kicad_pcb, board.kicad_sch, bom.csv, designators.csv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]
2026-06-07 mise a jour pcb routage pour reduire la taille
    [bom.csv, designators.csv, positions.csv]
2026-06-08 ajout etiquette global + plan de masse
    [board.kicad_pcb, board.kicad_sch]
2026-06-11 ajout empreinte STM8 + CH32V0003
    [board.kicad_pcb, board.kicad_sch, bom.csv, designators.csv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]
2026-06-12 correction inversion polarité sur l'alimentation
    [test.kicad_pcb, test.kicad_sch]
2026-06-20 mise a jour marquage pcb et ajout programation tiny dans le source, ajout autre famille ucontrolleur STM8 et wch
    [board.kicad_pcb, board.kicad_sch, positions.csv]
